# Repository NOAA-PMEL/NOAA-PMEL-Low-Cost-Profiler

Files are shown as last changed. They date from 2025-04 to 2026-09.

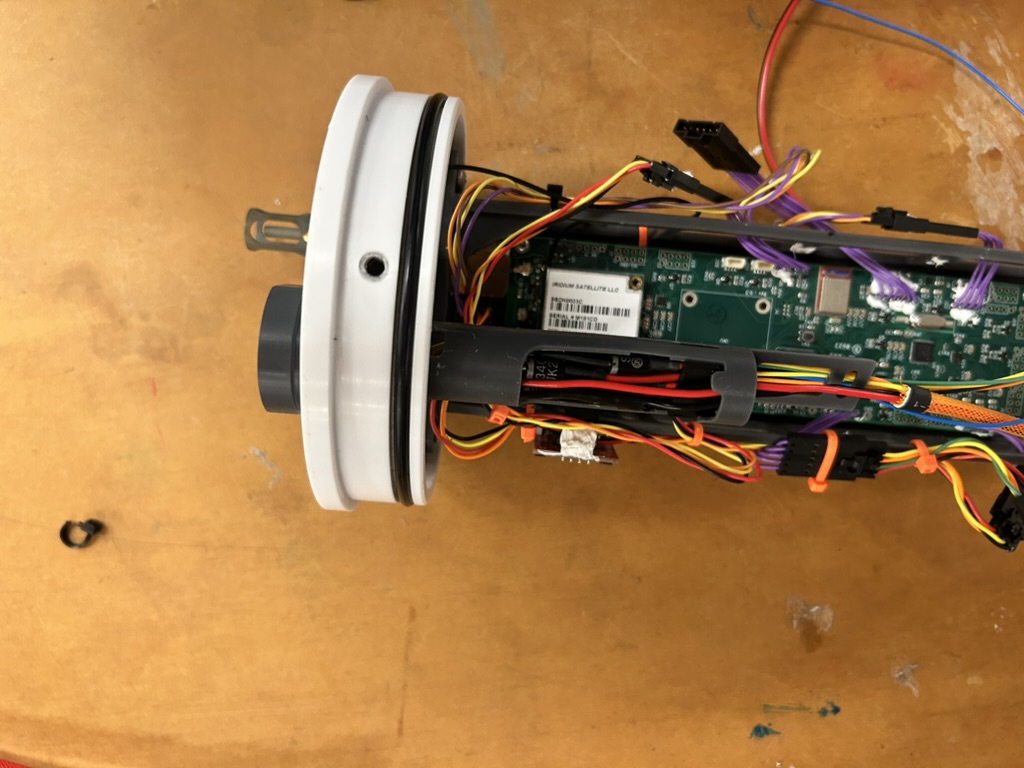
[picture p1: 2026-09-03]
Manual/UW Documents/Parts Photos/A83961EA-1B3E-4D60-9679-3123DDBCD0BC_1_105_c.jpeg

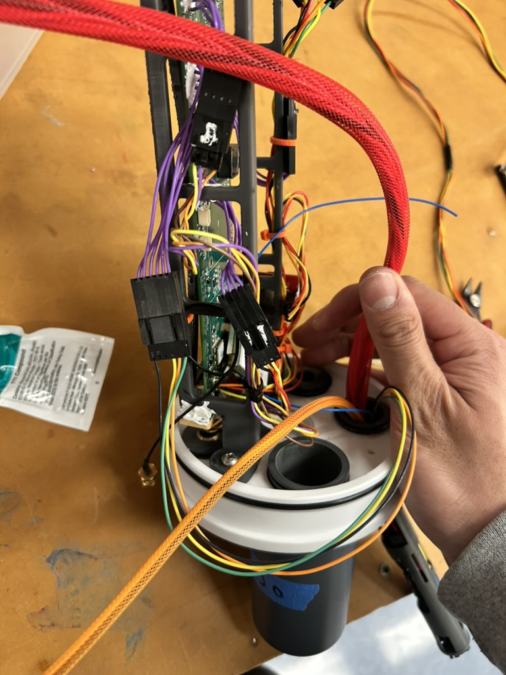
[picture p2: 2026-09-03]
Manual/UW Documents/Parts Photos/846BCBF3-054E-4CC3-9D93-AE1F20746E3C_1_105_c.jpeg

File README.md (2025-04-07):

# NOAA-PMEL Low Cost Profiler (LCP)
Open Source Repository for NOAA PMEL's Low Cost Profiler's mechanical design, firmware and electronics hardware.

# Attribution
You agree to acknowledge NOAA-PMEL on splash pages, and in publications, for products developed with this software.

# NOAA Legal Disclaimers
NOAA does not intend to patent this work, Low Cost Profiler (LCP) technology, worldwide. It may be used freely, but NOAA does not warrant its fitness for any use.

As a work of the United States Government, the associated schematics and software are in the public domain within the United States. Additionally, NOAA waives any potential copyright and related rights in the associated schematics and software worldwide through the Creative Commons Zero (CC0) 1.0 Universal Public Domain Declaration.

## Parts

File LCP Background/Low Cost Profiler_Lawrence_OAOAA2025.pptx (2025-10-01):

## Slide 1

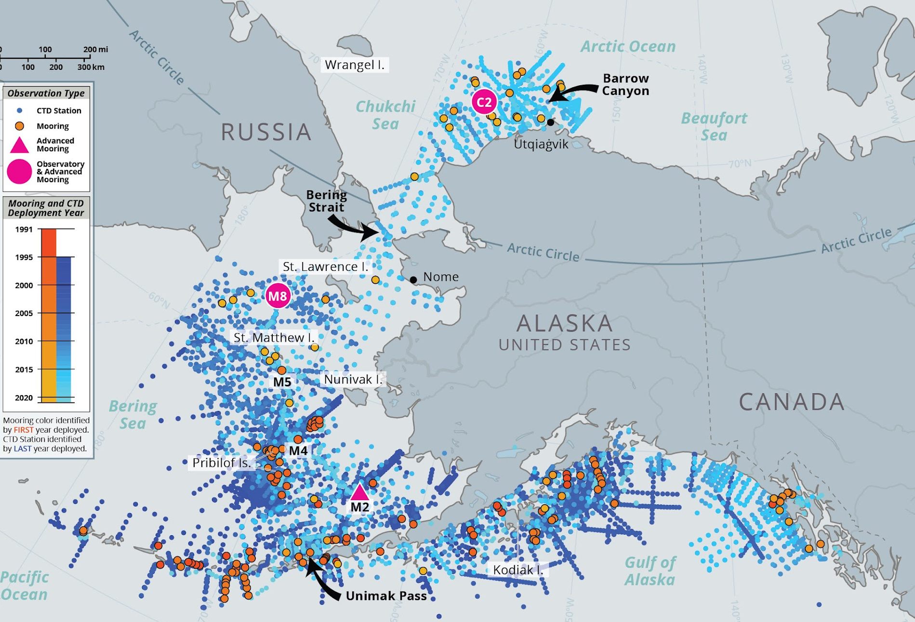
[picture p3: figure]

The Low Cost Profiler (LCP)
An affordable profiler to enable ocean science at scale

N.Lawrence¹, M. Casari², B.Martin¹, J.Kurina³
¹National Oceanic and Atmospheric Administration
²SeaMount Sensors & Automation, Waterbury, Vermont
³Cooperative Institute for Climate, Ocean, and Ecosystem Studies
PACIFIC MARINE ENVIRONMENTAL LAB | SEATTLE, WA

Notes: Mechanical Engineer at PMEL, what we do = design build and operate large global observational arrays = moorings
LCP was kickstarted by PMEL’s ITAE program = Innovative Technology for Arctic Exploration = Lab level, high risk High reward technology development funding to meet NOAA’s future ocean observation needs (other projects included Oculus and Saildrone)

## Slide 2

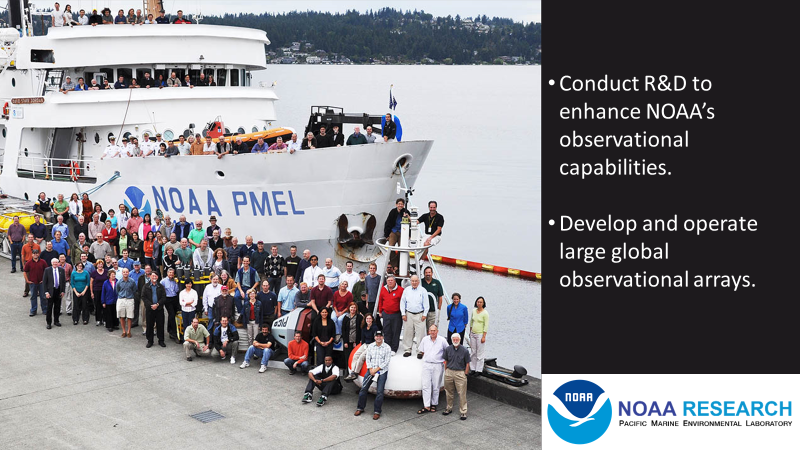
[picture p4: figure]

## Ocean Observation Tech Development: LCP

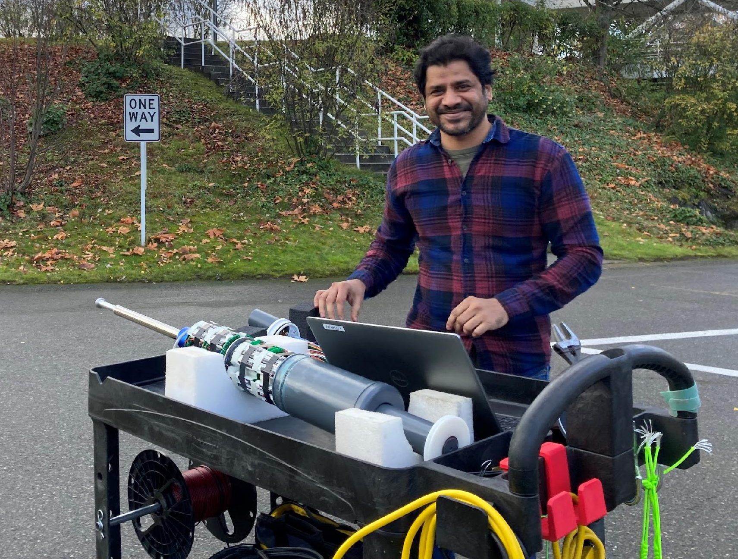
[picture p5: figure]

- LCP Product
- Science Applications
- Progress
- Future Plans/Needs

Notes: Quick rundown of this presentation

## Low Cost Profiler (LCP):

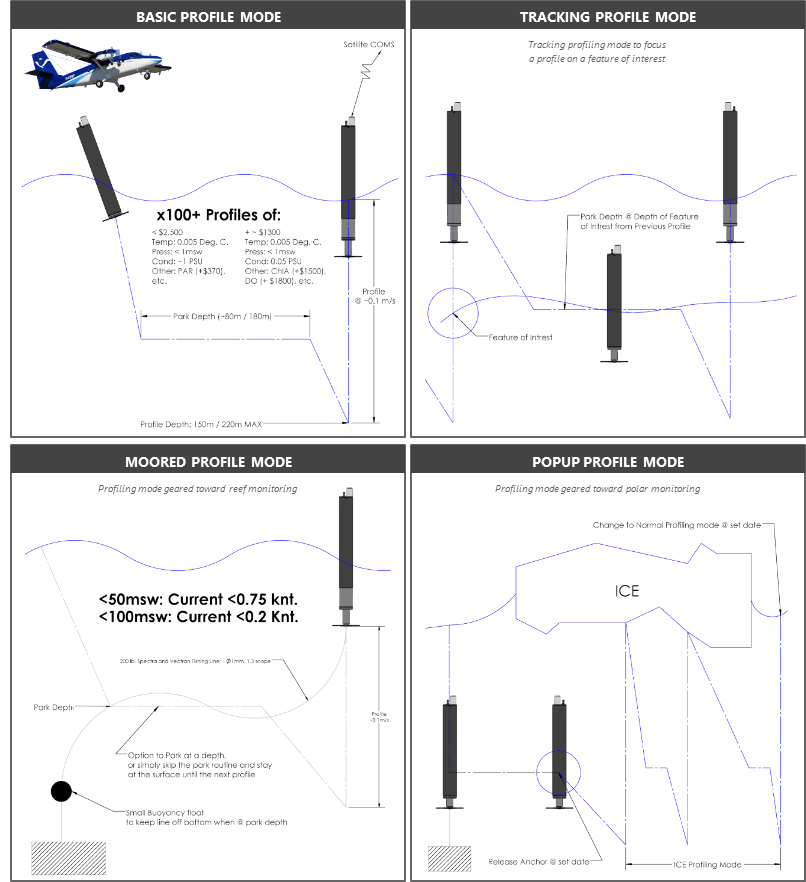
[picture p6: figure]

Cost | ~$5,000 (in QTYs of 10)
Maximum Depth | 220m
Endurance | 100 profiles (nominal)
Dimensions | 91.4 cm length x 12. 4 cm diameter
Weight | 13.6 kg
Telemetry | Iridium Short Burst Data (SBD) w/ more options available in future
Energy | Alkaline Battery Pack or Lithium
Features | Air deployable, Moorable
Sensors | Pressure: Keller 9LX-30Bar Temperature: S9 OEM Temp, RBRcoda* Conductivity:* S9 OEM CT, PMEL OEM, Aanderaa 5819 CHLA:* Turner Cyclops 7F PAR:* TAG-PARQ DO*: Aanderaa Optode 5730, PME microDOT

BASIC PROFILE MODE

BASIC PROFILE MODE

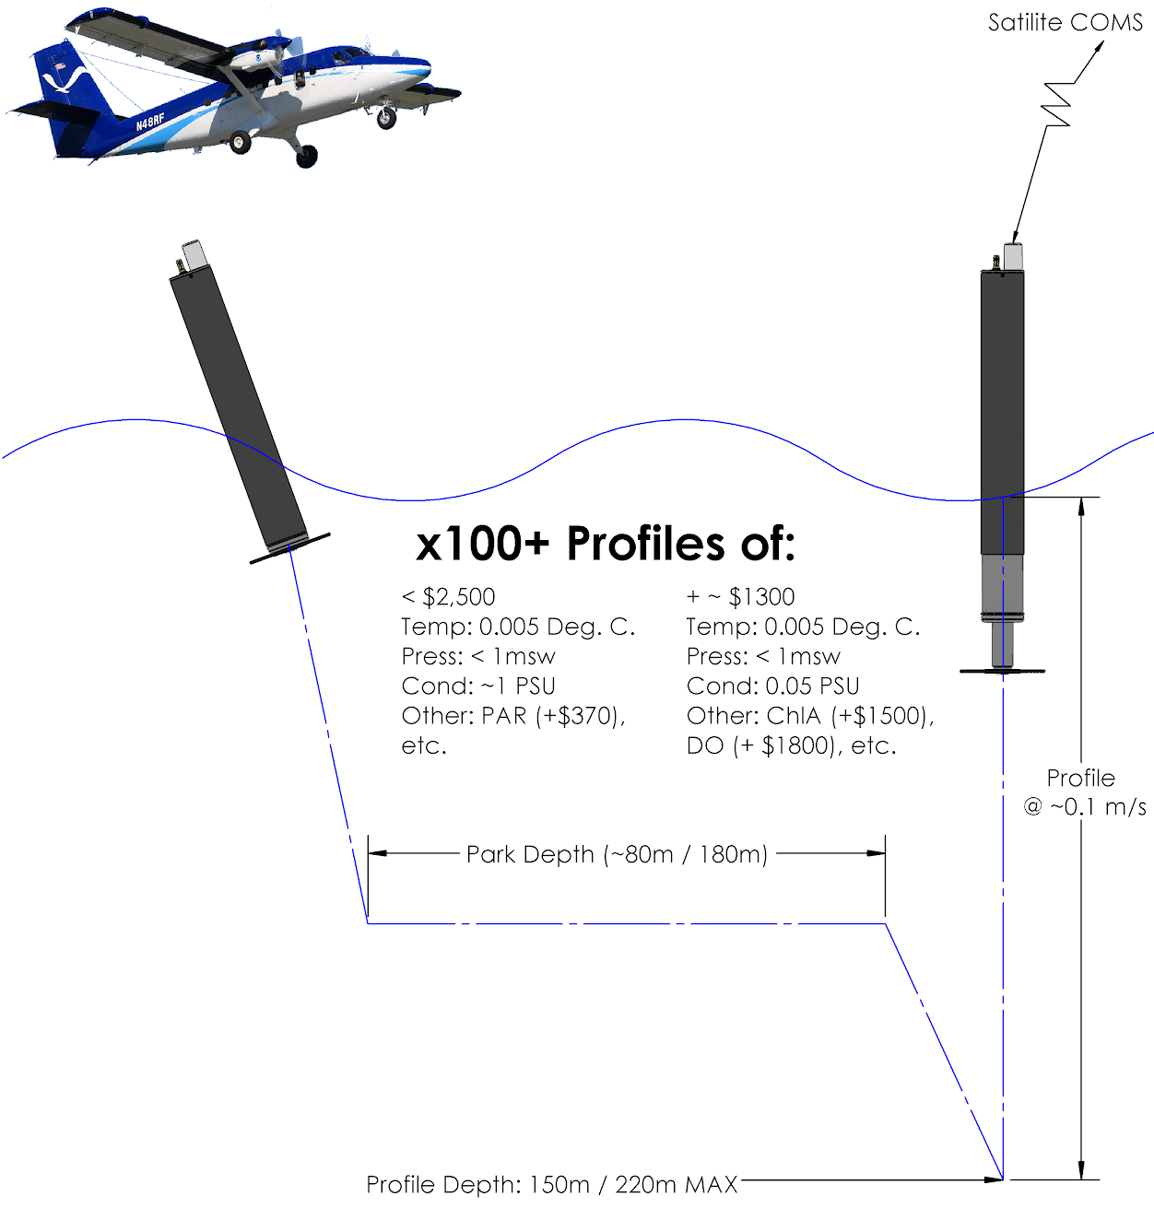
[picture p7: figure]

TRACKING PROFILE MODE

TRACKING PROFILE MODE

Tracking profiling mode to focus
a profile on a feature of interest

MOORED PROFILE MODE

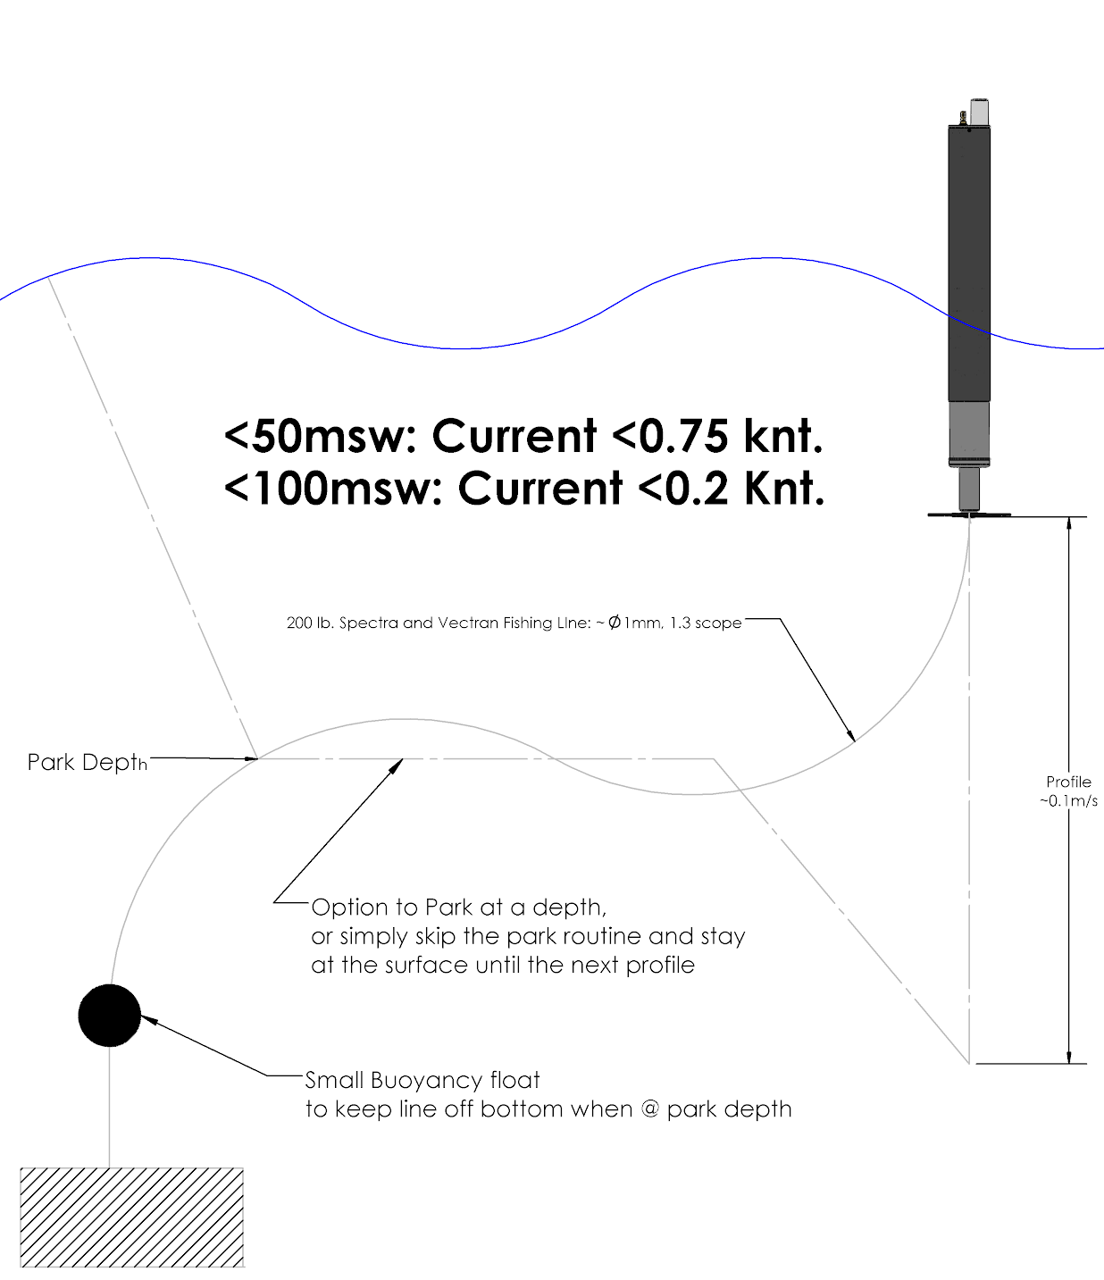
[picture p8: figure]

Profiling mode geared toward reef monitoring

POPUP PROFILE MODE

Profiling mode geared toward polar monitoring

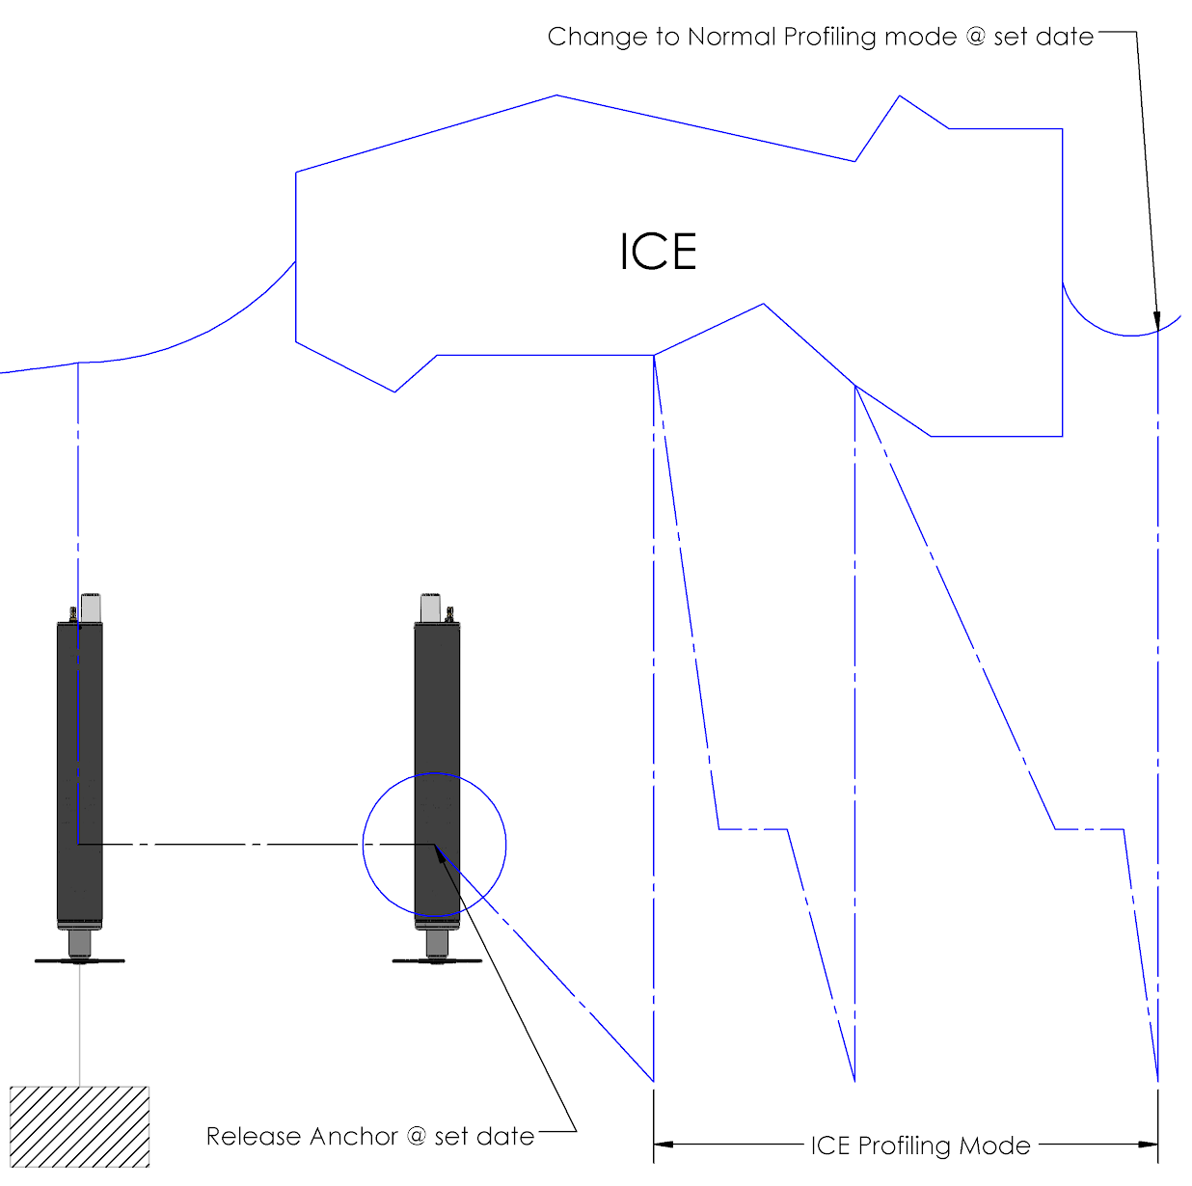
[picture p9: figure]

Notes: PMEL has developed the LCP, goal is to make a profile for <30$, an order of magnitude less than current profiling floats.
Developed to be easily built, configured, and deployed by air, ship or hand.
Simple Design = the LCP uses a direct-drive buoyancy engine to reduce mechanical complexity
Geared towards community involvement in sensor integration, goal is to bring your own sensor to an open source design that can be purchased from a contract manufacturer


The LCP can be configured pre-mission to perform in different observational roles, including drifting, timed release and moored, making it a unique tool for autonomously profiling the upper 200m of a water body.

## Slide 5

Low Cost Profiler (LCP): Sensors & Peripherals

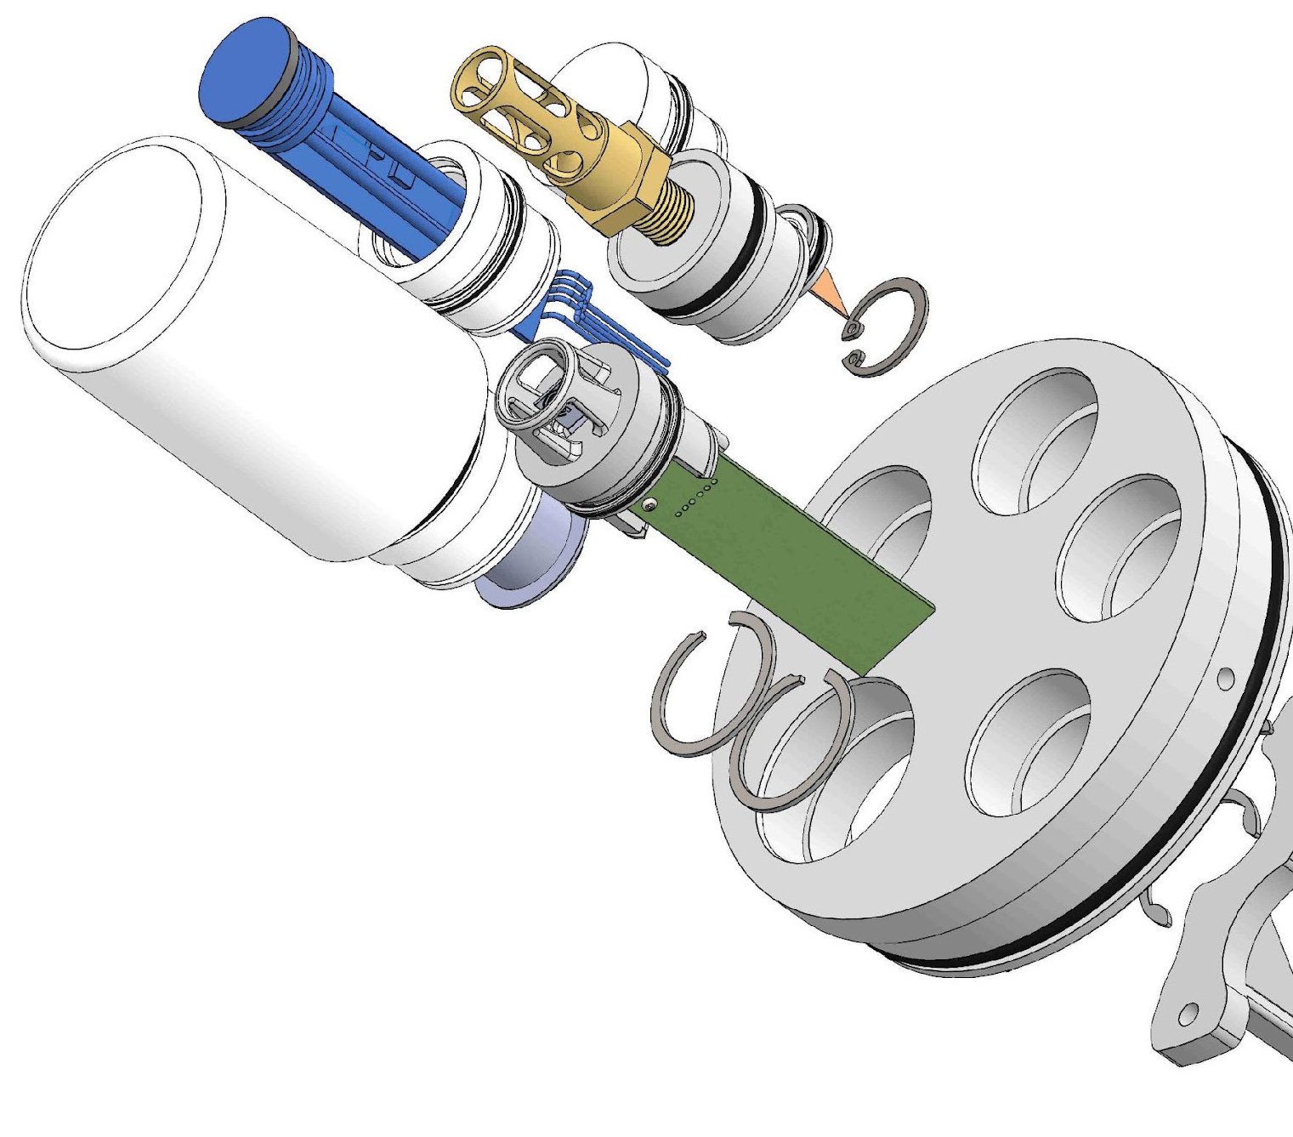
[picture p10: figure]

- OEM calibrated sensors
- 5 universal sensor ports
- Climate Quality
  - Temperature
  - Pressure
- ‘Weather’ Quality
  - Conductivity
  - CHL-A
  - PAR
  - DO
- Iridium SBD Communications

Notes: Key to reducing costs is using OEM manufacturer calibrated sensors

## LCP: Science Driven Applications

LCP Fills Gaps in Observational Arrays

Graphic Courtesy of Adrienne Sutton

- Hurricane Intensity
- Bering Sea Fisheries
- Arctic HABs and Ice
- Coastal & Coral Reef Monitoring
- ONR Profiling CTD BAA

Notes: Observation challenge = work to do to reduce the uncertainty in our predictive capability = opportunity for technology innovation in our flat funded world!
In response to this challenge, NOAA-PMEL is exploring innovative methods to quickly propagate and support high quality, low cost, tools throughout our community.
Requires the development of fit-for-purpose tools to fill gaps in our traditional observational array
LCP Solution =
Multi-mission capable = capitalize on economies of scale.
Keep costs low to allow for risk taking and rapidly scale in situ observations
Sensors are very expensive = make profiles
Profiling floats have proven successful at covering large volumes, ARGO like…. but much cheaper
Relevance & Application Examples: LCP has wide applicability to many NOAA R&D vision areas and the 2026 strategic research guidance memorandum
Vision Area 1: Hazardous and Extreme Weather = Hurricane Intensity
Vision Area 2: Sustainable fisheries
SRGM: improve coverage of observations = gap filling & Arctic & HAB

Here are a few we are actively pursuing that address , others? Let’s talk = rely on word of mouth for tech dissemination.

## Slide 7

LCP: Hurricane Application

GOAL: Subsurface ocean temperature and salinity measurements are needed ahead of and underneath hurricanes to:
- Initialize coupled forecast models
- Improve mixing parameterizations in models
- Aid forecaster situational awareness
- Improve understanding of hurricane air-sea interaction processes

Existing Technology:
- ALAMO Float = Expensive: ~$400K for 16 floats deployed ahead of Hurricanes Irma and Florence
- AxBT & AxCTD = Less expensive (~$1000) but only gives one temperature or CTD profile
Partner: AOML (Jun Zhang, Greg Foltz)

Three-dimensional cartoon of the temperature distribution in the upper ocean and the impact of a hurricane passing over the ocean when the oceanic mixed layer is thin like in the Gulf of Mexico and thick like the Caribbean Sea.

Credit: National Geographic

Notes: Hurricanes intensify by drawing heat energy from the ocean, Strong ocean mixing by a hurricane’s winds brings cooler water to the surface, decreasing the heat energy available to the hurricane
Air deployable LCP application

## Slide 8

LCP: Fisheries Application

GOAL: Improve understanding of regional oceanography and support fishing industry with tools that may reduce halibut bycatch

Need understand the connection between surface temperature and bottom temperature in the Kuskokwim Bay area, so that we may be able to use remotely-sensed surface temperature to predict real-time bottom temperature.
Partner: PMEL-ECOFOCI (Phyllis Stabeno, Calvin Mordy)


Predicting these bottom temperatures is difficult!
Measuring bottom temperature with LCP will support fishing industry


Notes:
Improve understanding of regional oceanography and (2) support fishing industry with predictive tools that may help reduce halibut bycatch
Yellowfin sole arrive earlier in colder water than halibut. To avoid halibut bi-catch it is necessary to predict (or measure) bottom temperatures. Allowing fishing vessels to arrive at fishing grounds when bottom temperatures are more optimal for yellowfin sole and less optimal halibut
Application for moored LCP, will trial this technology in Fall 2025

S = Spring when Yellowfin arrive on the inner shelf while temps are too cold for halibut. As things warm the fleet needs to move to colder water to avoid catching the halibut. Yellowfin move to deeper water if fall (F) and winter (W)

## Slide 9

Low Cost Profiler: Current Status


- Complete:
  - mechanical stress testing.
  - functional testing in tank.
  - Hand-deployed at RL5
- Now:
  - 5x field deployments moored in Puget Sound, WA.
  - Completed 100 profiles to 170m.
- Next Steps:
  - Secure stage 2 funding
  - CTD Sensor Integration
  - Air Deployment- ONR BAA
  - Open Source approach


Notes: Design is proven in PMEL pressure vessel and NOAA Dive Tower
Moored in Puget Sound
Next Steps = Secure funding for 2 focus areas for continued LCP tech development

## LCP expands work in the Beaufort Sea

LCP: Arctic Sea Ice Application

- Arctic AIR (Jiaxu Zhang, UW-CICOES) focuses on stratification mechanisms in the southern Beaufort Sea and their impact on sea ice formation/melt and phytoplankton growth.
- Previously, we relied on AxCTDs and ALAMO floats for this data, but LCP offers a more cost-effective alternative for measuring salinity-driven stratification.


2024 AxBT deployment along 150W


An ALAMO drifting down from Twin Otter

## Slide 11

Open Source Solution:

Societal implications of ocean change ≠ capacity of ocean technology development community


      - Use: Provide truly low-cost tool
- Scale: Contract manufacturer approach to building in quantities
- Sustain: Industry and users can assist in system upgrades, sensor integration…..


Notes:
Use LCP as a pilot for Open Source approach
Tool is not very useful if it is not available, how do we rapidly get the LCP technology into the hands of the broader scientific community?
Problem= Ocean observing technology development life cycles are too long!
Problem= Traditional commercialization path can result in expensive products that receive inadequate sustained development support
Problem = Sole source single points of failure =products often dropped due to lack of adequate commercial sales


Have been working with NOAA’s Tech Partnership office to:
Generate open source hardware license
Develop an open source technology transfer pathway in NOAA
Obtain permission to open source
MBARI has had a lot of luck with contract manufacturers producing complicated ocean sensors (pH), could be a solution to providing community with a source, this is what they are good at. Community ecosystem could then provide buying power, functionality upgrades
Risk = Do not know if it will work.

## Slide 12


Thank You

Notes:
Thank you!

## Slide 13


Low Cost Profiler (LCP): Design


- Simple direct drive buoyancy engine
- Maximizes OEM components
- Minimizes custom components

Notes: The LCP uses a direct-drive buoyancy engine to reduce mechanical complexity
And a commodity pressure housing taken from the industrial pneumatics industry

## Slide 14

ALAMO floats
Deployed ahead of hurricanes by aircraft
Can profile every 2 hours to 300 m for several months
Expensive: ~$400K for 16 floats deployed ahead of Hurricanes Irma and Florence

Sanabia and Jayne (2020)

Details are in the caption following the image

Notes: First row of colored circles indicates float deployment locations. Subsequent circles show surfacing locations of the floats, with colors indicating measured SST as the hurricane passed.

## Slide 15

AXBTs
Deployed ahead of hurricanes by aircraft
Floats on surface, releases thermistor probe that measures temperature as it drops
Less expensive (~$1000) but only gives one temperature profile
AXCTDs also measure salinity but are more expensive

Images showing an AXBT instrument and how the instrument is launched.

Credit: U.S. Coast Guard

NOAA Measures Hurricane Tammy from Satellites through the Sea

## LCP adds an additional platform for HAB monitoring

LCP: HAB Application

- Arctic AIR (Jiaxu Zhang, UW-CICOES) and collaborators are developing a multi-platform phytoplankton monitoring system to enable early warning of harmful algal blooms (HABs) in the Pacific Arctic.
- LCP with additional light and biological sensors (e.g, PAR, Chl-a) will greatly enhance data collection and help us better understand biophysical interactions and primary production.


LCP

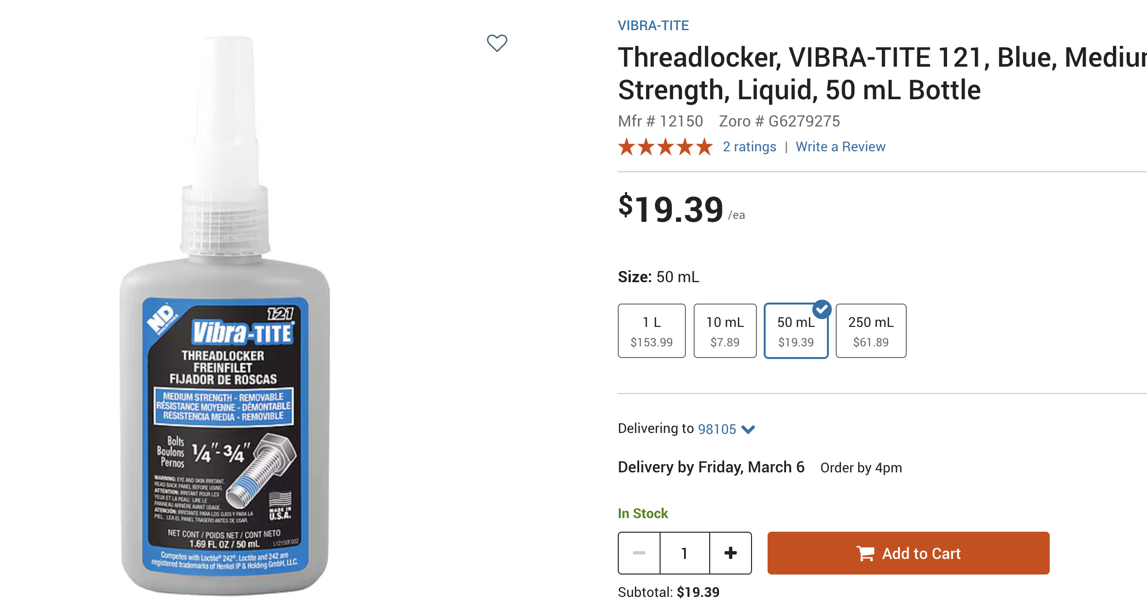
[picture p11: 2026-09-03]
Manual/UW Documents/Parts Photos/Screenshot 2026-03-04 at 11.32.21 AM.png

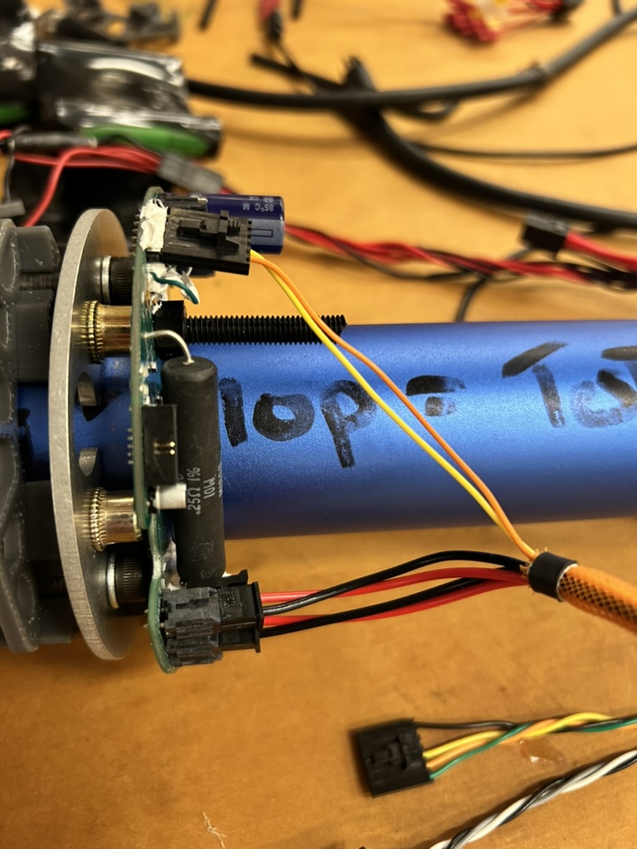
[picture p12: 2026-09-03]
Manual/UW Documents/Parts Photos/684DF367-D09E-419C-A230-30884F840D1B_1_105_c.jpeg

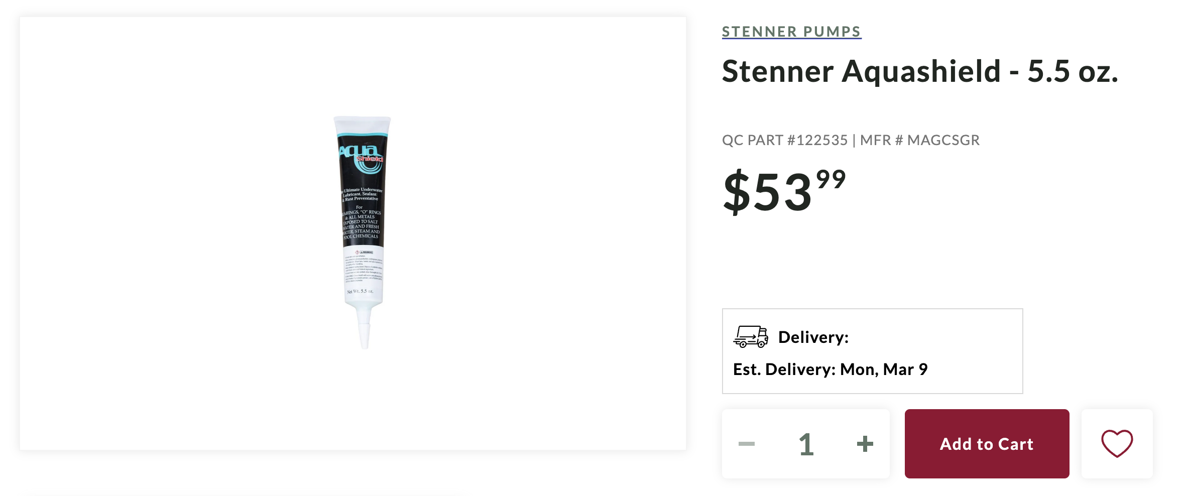
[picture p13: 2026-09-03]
Manual/UW Documents/Parts Photos/Screenshot 2026-03-04 at 11.31.39 AM.png

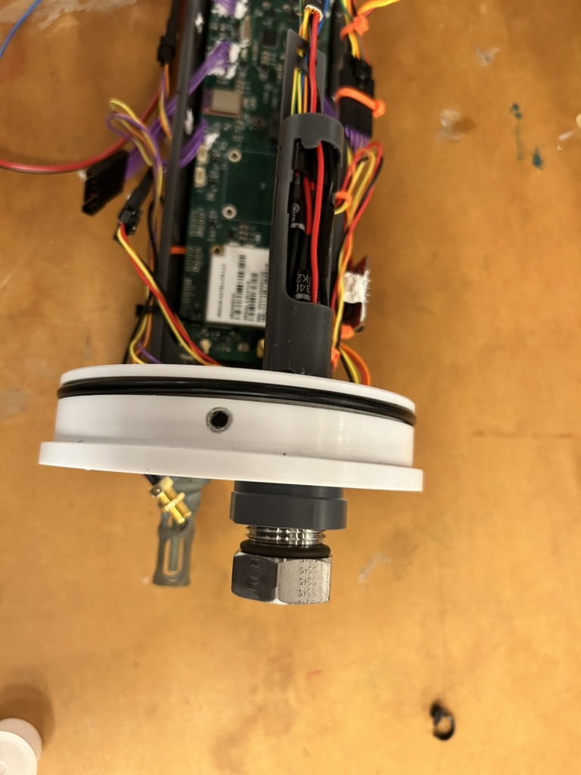
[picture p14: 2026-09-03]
Manual/UW Documents/Parts Photos/04B5F0DC-DED3-4595-93C2-F169555D24E7_1_105_c.jpeg

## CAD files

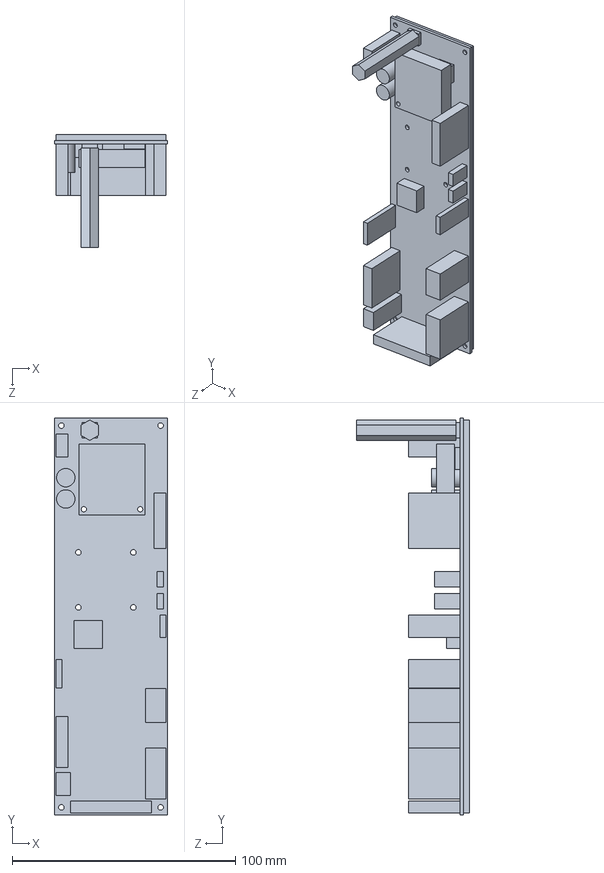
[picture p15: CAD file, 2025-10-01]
Mechanical/EDD Circuit Boards/R_Low Cost Profiler Main Control Board.sldprt
50.8 x 177.8 x 50.4 mm

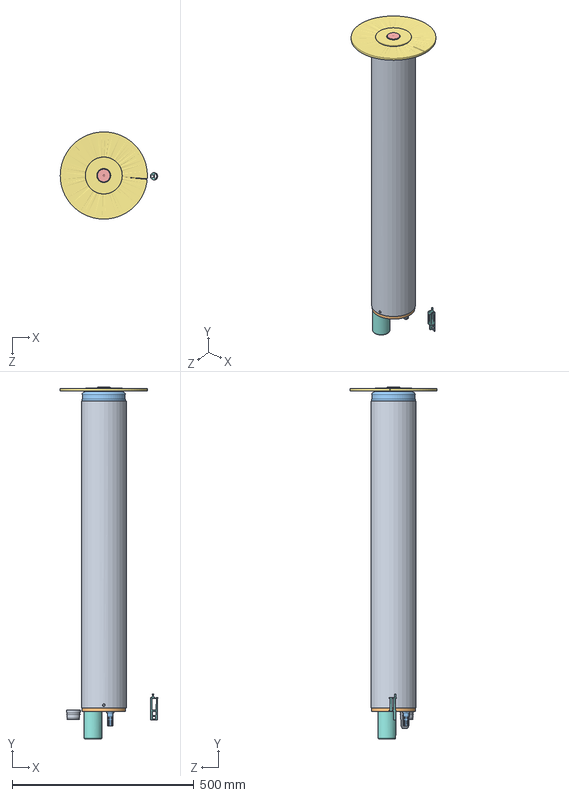
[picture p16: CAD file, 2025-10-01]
Mechanical/CAD Detail Parts/R_500140.sldasm
268.3 x 968.2 x 239.6 mm
FA-BH50-XXX-12-12
89U140341TT0667 x 2
98455A161_INTERNAL RETAINING RING
95105A183_ZINC-PLATED STEEL HEAVY-DUTY RIVET NUT x 8
Zeus_AA_ Alkaline_Battery x 72
Low Cost Profiler 9 Cell AA Battery Board x 16
92120A150_BRASS HEAT-SET INSERTS FOR PLASTIC x 66
92095A322_BUTTON HEAD HEX DRIVE SCREW x 66
91290A155_BLACK-OXIDE CLASS 12.9 SOCKET HEAD CAP SCREW x 4
91166A250_ZINC-PLATED STEEL FLAT WASHER x 4
90576A115_ZINC-PLATED CLASS 8 STL NYLON-INSERT LOCKNUT x 2
98455A224_INTERNAL RETAINING RING
97414A705_LOW CLEARANCE EXTERNAL RETAINING RING x 4
91650A490_18-8 SS SPIRAL EXTERNAL RETAINING RING
93369A141_NYLON HEX NUT x 4
Keller 9LX Pressure Sensor
92981A309_ALLOY STEEL SHOULDER SCREW
95610A370_NYLON PLASTIC WASHER_ x 4
2110-000-C-NH
92290A139_TYPE 316 SS SOCKET HEAD CAP SCREW x 2
HC600E
92131A630_SINGLETURN SPIRAL INTERNAL RETAINING RING x 2
98555A230_LOW-CLEARANCE EXTERNAL RETAINING RING
Low Cost Profiler Main Control Board
9452K840_OIL-RESISTANT BUNA-N MULTIPURPOSE O-RING x 4
9452K890_OIL-RESISTANT BUNA-N MULTIPURPOSE O-RING
9452K194_OIL-RESISTANT BUNA-N MULTIPURPOSE O-RING
94241A520_TYPE 316 STAINLESS STEEL SPLIT LOCK WASHER x 2
0307-PDT-H-093-0250 x 3
Parker_N4274_250_04000
Parker_N4274_250_02250
LFS1K011076WB010_6S
IST Conductivity Board
Low Cost Profiler Battery Power Management Board
SoundNine_Digital_OEM_Temperature_Sensor
SparkFun_Openlog_Qwiic
Maxtena_M1621HCT_P_SMA

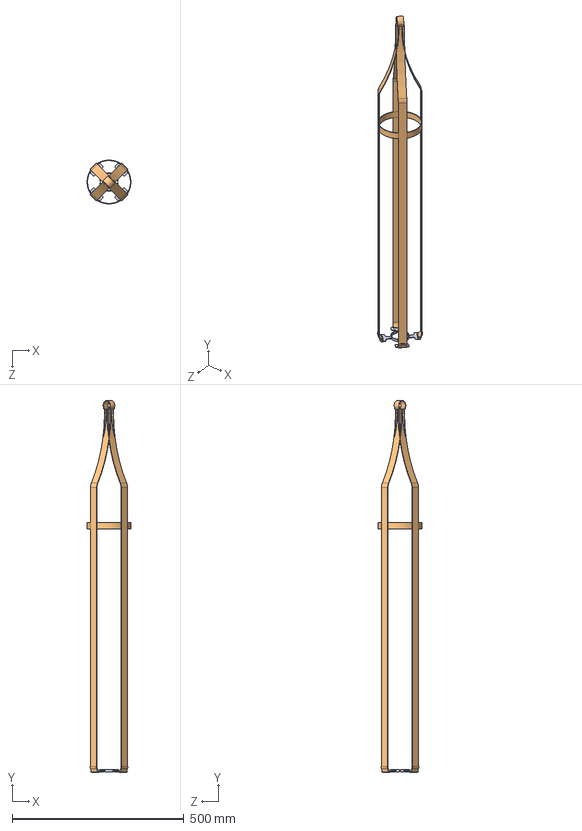
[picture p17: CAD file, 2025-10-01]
Mechanical/CAD Detail Parts/R_500151.sldasm
127.6 x 1082.7 x 127.6 mm

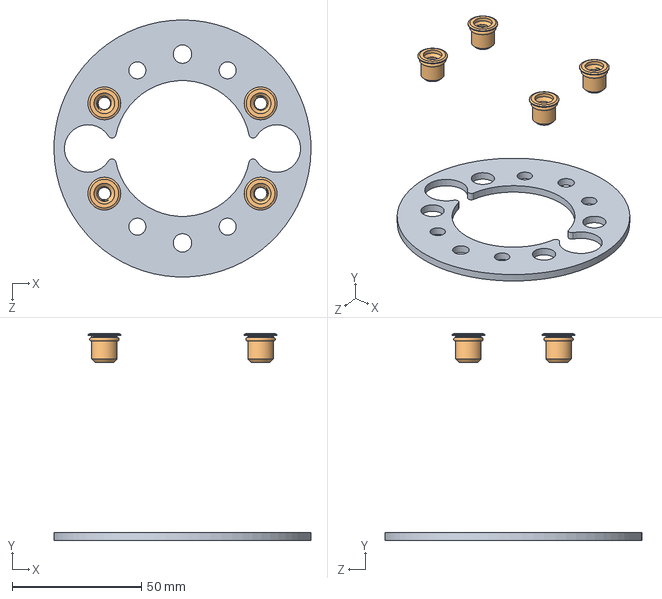
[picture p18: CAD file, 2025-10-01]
Mechanical/CAD Detail Parts/R_500142.sldasm
99.5 x 80.2 x 99.5 mm
95105A183_ZINC-PLATED STEEL HEAVY-DUTY RIVET NUT x 4

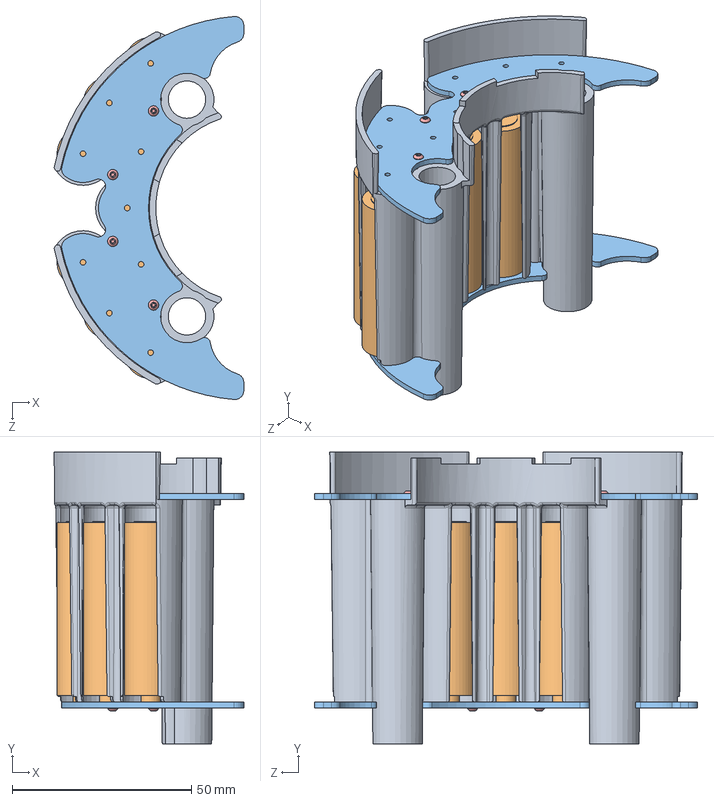
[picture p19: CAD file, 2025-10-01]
Mechanical/CAD Detail Parts/R_500147.sldasm
53.0 x 81.4 x 106.9 mm
Zeus_AA_ Alkaline_Battery x 9
Low Cost Profiler 9 Cell AA Battery Board x 2
92120A150_BRASS HEAT-SET INSERTS FOR PLASTIC x 8
92095A322_BUTTON HEAD HEX DRIVE SCREW x 8

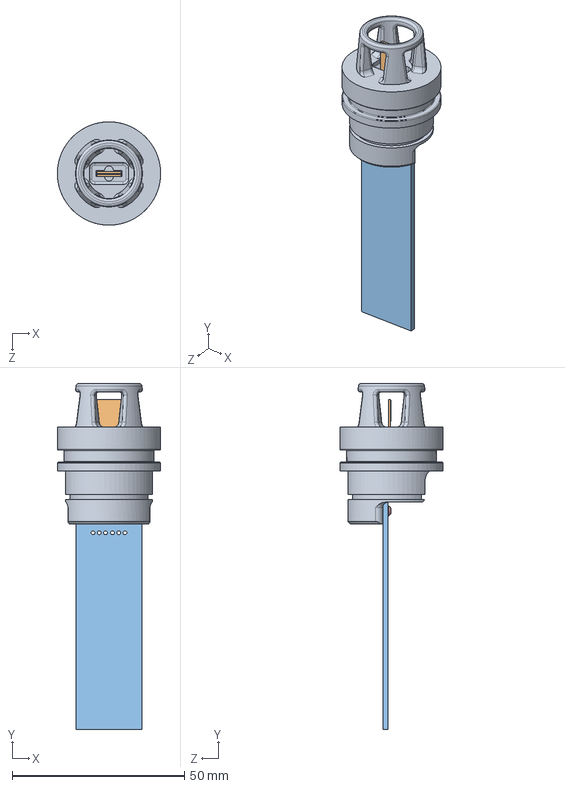
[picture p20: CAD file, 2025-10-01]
Mechanical/CAD Detail Parts/R_500126.sldasm
30.0 x 100.5 x 30.0 mm
LFS1K011076WB010_6S
IST Conductivity Board
92120A150_BRASS HEAT-SET INSERTS FOR PLASTIC x 2
92095A322_BUTTON HEAD HEX DRIVE SCREW x 2

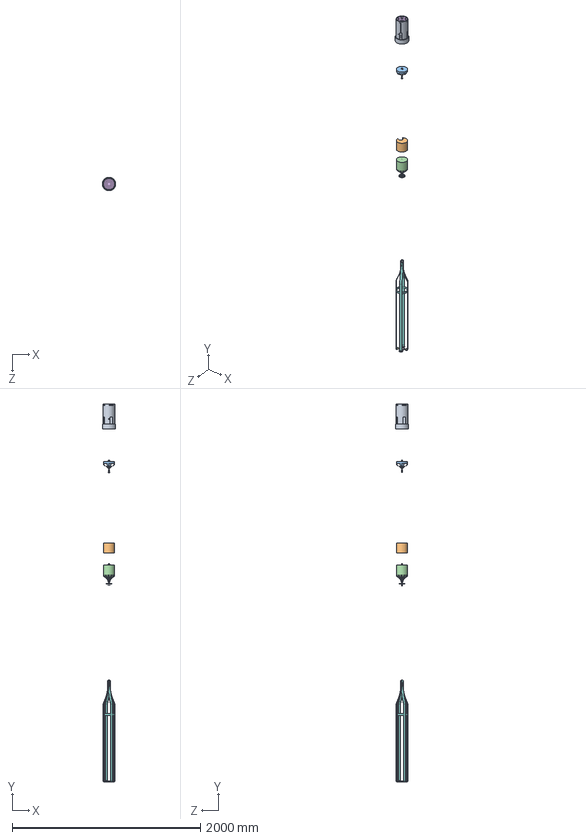
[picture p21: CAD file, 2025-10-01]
Mechanical/CAD Detail Parts/R_500150.sldasm
142.9 x 4012.2 x 143.0 mm
Rocketman_Pro-X_18in_Parachute
Rocketman_High Performance Chute_60in
3769T77_STAINLESS STEEL RING-NOT FOR LIFTING

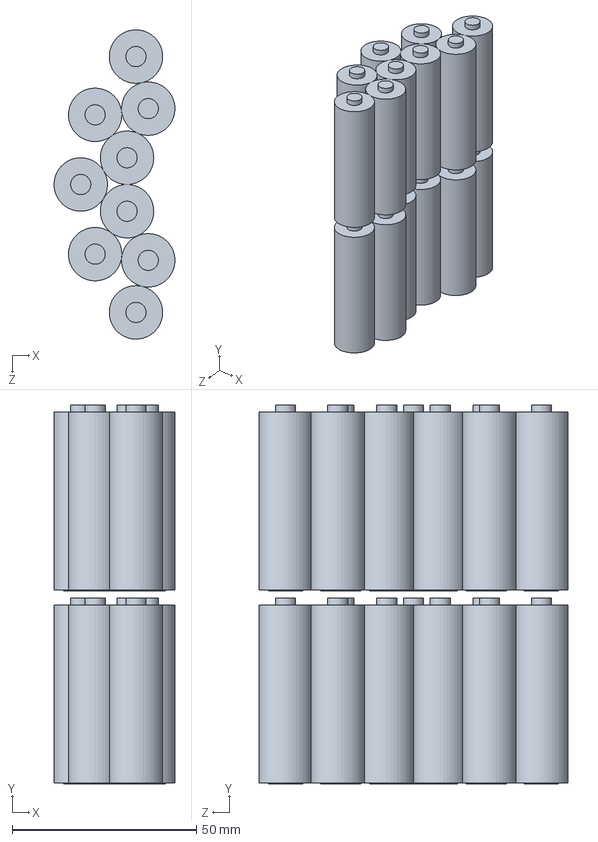
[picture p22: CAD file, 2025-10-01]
Mechanical/CAD Detail Parts/R_500146.sldasm
32.8 x 102.8 x 83.9 mm
Zeus_AA_ Alkaline_Battery x 18

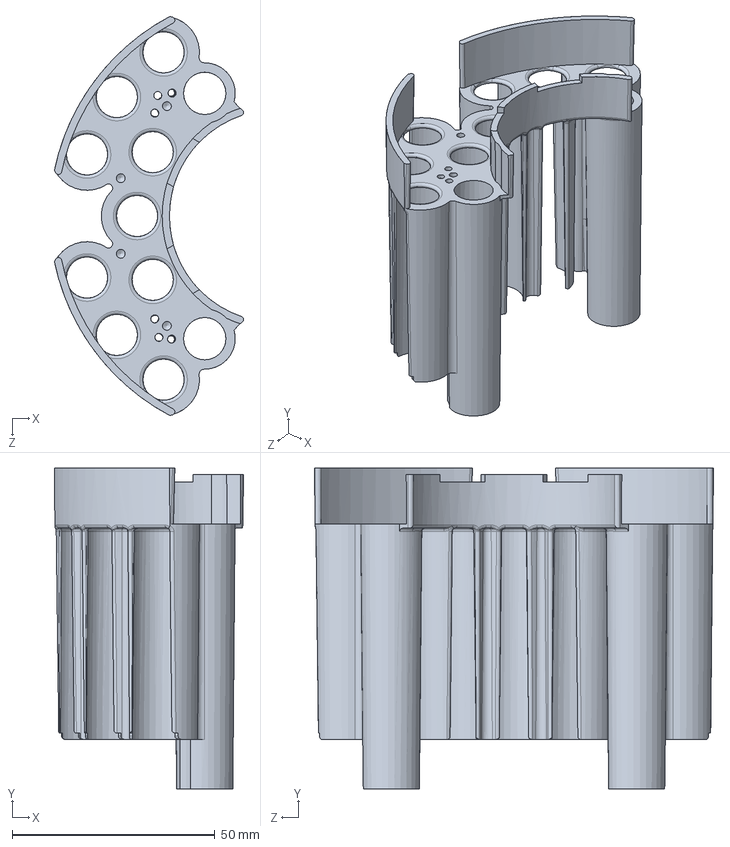
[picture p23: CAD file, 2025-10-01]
Mechanical/CAD Detail Parts/R_000550.SLDPRT
46.7 x 79.1 x 98.4 mm

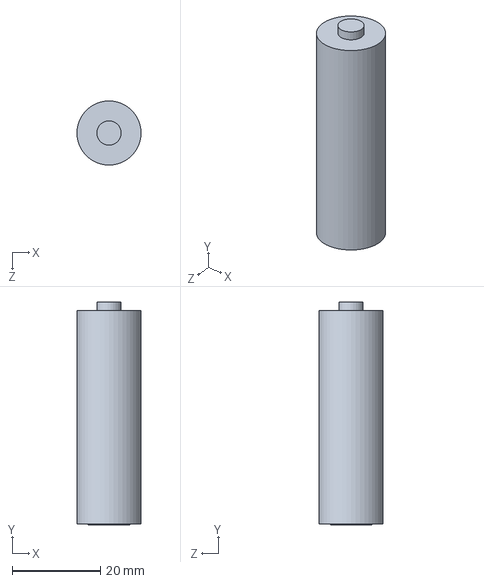
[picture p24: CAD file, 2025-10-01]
Mechanical/CAD OEM/R_Zeus_AA_ Alkaline_Battery.sldprt
14.5 x 50.4 x 14.5 mm

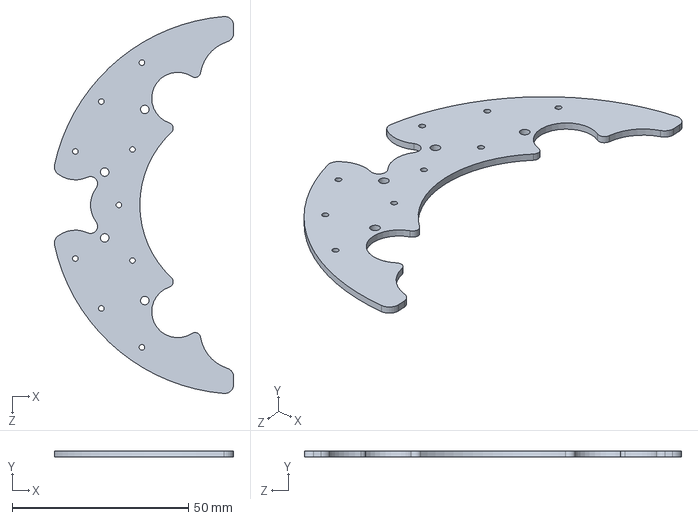
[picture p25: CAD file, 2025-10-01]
Mechanical/EDD Circuit Boards/R_Low Cost Profiler 9 Cell AA Battery Board.sldprt
50.9 x 1.60 x 106.9 mm

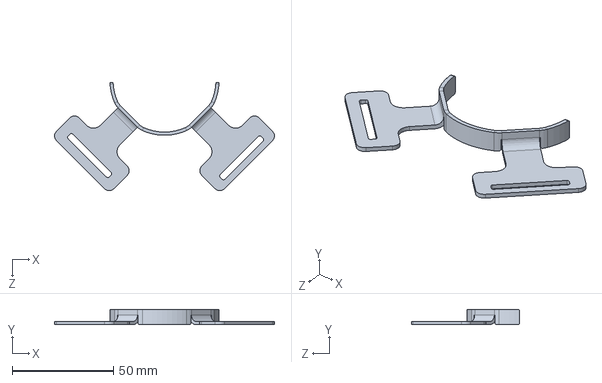
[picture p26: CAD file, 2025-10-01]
Mechanical/CAD Detail Parts/R_000561.SLDPRT
108.8 x 7.62 x 53.6 mm

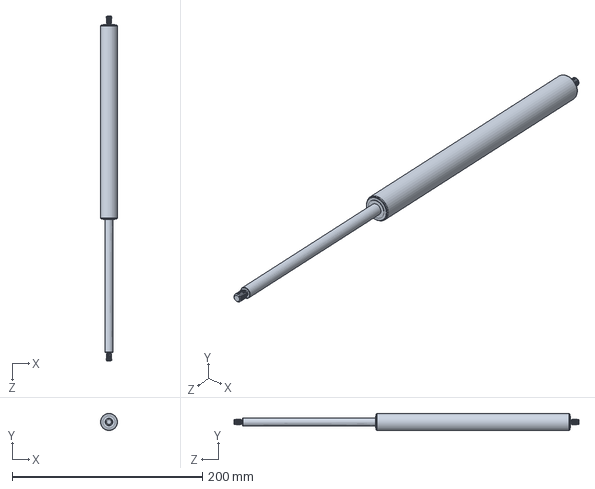
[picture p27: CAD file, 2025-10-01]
Mechanical/CAD OEM/R_89U140341TT0667.SLDPRT
18.0 x 18.0 x 362.9 mm

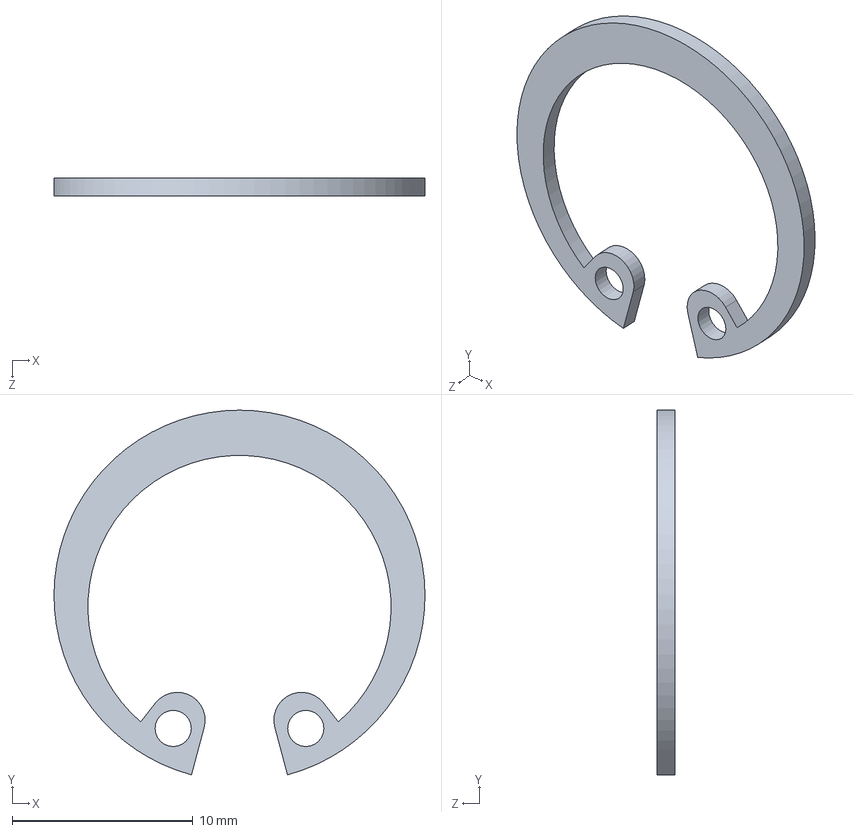
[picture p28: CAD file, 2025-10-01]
Mechanical/CAD OEM/R_98455A224_INTERNAL RETAINING RING.SLDPRT
20.5 x 20.2 x 1.00 mm

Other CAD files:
Mechanical/EDD Circuit Boards/R_002166.SLDPRT
Mechanical/CAD Detail Parts/R_000524.sldprt
Mechanical/EDD Circuit Boards/R_Low Cost Profiler Battery Power Management Board.SLDPRT
Mechanical/CAD Detail Parts/R_000549.sldprt
Mechanical/CAD Detail Parts/R_000450.SLDDRW
Mechanical/CAD Detail Parts/R_000450.sldprt
Mechanical/CAD Detail Parts/R_000521.SLDDRW
Mechanical/CAD Detail Parts/R_000521.sldprt
Mechanical/CAD Detail Parts/R_000522.SLDDRW
Mechanical/CAD Detail Parts/R_000522.sldprt
Mechanical/CAD Detail Parts/R_000524.SLDDRW
Mechanical/CAD Detail Parts/R_000525.SLDDRW
Mechanical/CAD Detail Parts/R_000525.sldprt
Mechanical/CAD Detail Parts/R_000529.SLDDRW
Mechanical/CAD Detail Parts/R_000529.sldprt
Mechanical/CAD Detail Parts/R_000531.SLDDRW
Mechanical/CAD Detail Parts/R_000531.sldprt
Mechanical/CAD Detail Parts/R_000532.SLDDRW
Mechanical/CAD Detail Parts/R_000532.sldprt
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

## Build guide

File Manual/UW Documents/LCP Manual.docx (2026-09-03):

# Table of Contents

Low-Cost Profiler Manual

Table of Contents -------------------------------------------------------- 1

Parts List ------------------------------------------------------------------ 2

Tool List ------------------------------------------------------------------- 3

Inner Assembly ---------------------------------------------------------- 4

Outer Assembly ---------------------------------------------------------- 5

Sensor Cap Assembly --------------------------------------------------- 6

Flashing the Control Board -------------------------------------------- 7

# Parts List

# Parts List

# Inner Assembly Parts:

Part Number | Part Name | Description | Stock size | Vendor+link | Quantity | image | Git number
1 | FA-BH50-XXX-12-12 | Firgelli Bullet Series 50 Cal. Linear Actuator, 12" stroke | FA-BH50-XXXX-12-12 | Firgelli Automation part site (https://www.robotshop.com/products/bullet-series-50-cal-linear-actuators-12v-500lb-12-inch?gad_source=1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) | 1 | | 4

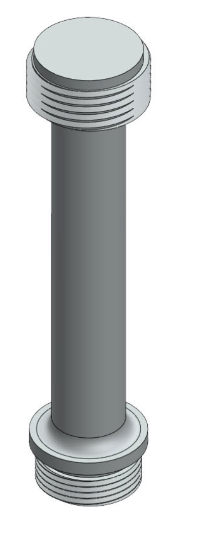
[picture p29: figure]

2 | Actuator Mount | Two sided threaded mount | | part file (https://github.com/NOAA-PMEL/NOAA-PMEL-Low-Cost-Profiler/blob/main/Mechanical/Mechanical%20Build%20Notebook/000532%20-%20Sheet1.pdf) | 1 | | 36

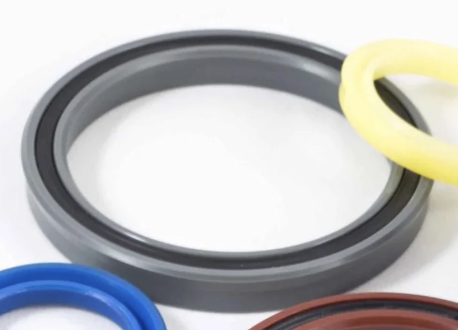
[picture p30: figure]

3 | N4274_250_02250 | 2.25" ID Parker PolyPak SPP Hydraulic Seal | N4274-250-02250 | Parker part link (https://www.parker.com/content/dam/Parker-com/Literature/Engineered-Polymer-Systems/EPS5370_PNLOOKUP.pdf) | 1 | | 46
4 | 000524 | Low Cost Profiler Piston #1 | PVC Type I Rod 1 | In house part file (https://github.com/NOAA-PMEL/NOAA-PMEL-Low-Cost-Profiler/blob/main/Mechanical/Mechanical%20Build%20Notebook/000524%20-%20Sheet1.pdf) | 1 | | 3
5 | N4274_250_04000 | 4" ID Parker PolyPak SPP Hydraulic Seal | N4274-250-04000 | Parker part link (https://www.parker.com/content/dam/Parker-com/Literature/Engineered-Polymer-Systems/EPS5370_PNLOOKUP.pdf) | 1 | | 45

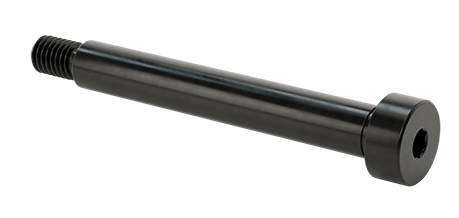
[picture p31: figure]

6 | 92981A309_ALLOY STEEL SHOULDER SCREW | M8 x 1.25mm, 10mm Dia x 70mm L, Shoulder Screw | 92981A309 | McMasterCarr part link (https://www.mcmaster.com/products/shoulder-screws/thread-size~m8-2/thread-pitch~1-25-mm/) | 1 | | 25

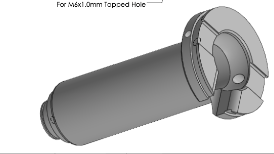
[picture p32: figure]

7 | 000525 | Low Cost Profiler Piston #2 | | part file (https://github.com/NOAA-PMEL/NOAA-PMEL-Low-Cost-Profiler/blob/main/Mechanical/Mechanical%20Build%20Notebook/000525%20-%20Sheet1.pdf) | 1 | | 5
8 | 0307-PDT-H-093-0250 | 7.31" Long 0307-PDT-H-093-0250 | 7.31" Long | Parker part link (https://ph.parker.com/us/en/product/cut-to-length-ptfe-wear-strip-for-pistons-pdt/0307-pdtb-02250-a-xxxx) | | | 42
9 | 0307-PDT-H-093-0250 | 11.44" Long 0307-PDT-H-093-0250 | 11.44" Long | Parker part link (https://ph.parker.com/us/en/product/cut-to-length-ptfe-wear-strip-for-pistons-pdt/0307-pdtb-02250-a-xxxx) | | | 44

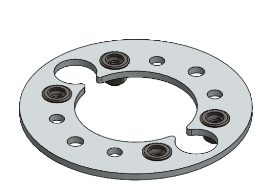
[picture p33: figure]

10 | 500142 | Low Cost Profiler Gas Spring Ring | | Part file (https://github.com/NOAA-PMEL/NOAA-PMEL-Low-Cost-Profiler/blob/main/Mechanical/Mechanical%20Build%20Notebook/500142.pdf) | 2 | | 13
11 | 98455A161 | 100mm Steel Internal Retaining Ring | MMC# 98455A161 | McMasterCarr part link (https://minibearings.com/products/100x103-5x3-internalcirclips-cci10000c) | 1 | | 7
12 | 89U140341TT0667 Gas Springs | IGS 8/18 x 140mm Gas Spring | | Industrial Gas Spring part link (https://www.raptorsupplies.com/pd/spd/89u140341tt0667) | 2 | | 6
13 | 90576A115 | M6 x 1mm, Medium-Strength Steel Nylon-Insert Locknut | 90576A115 | McMaster Carr part link (https://www.mcmaster.com/products/class-8-steel-hex-nuts/locknuts-2~/?s=class-8-steel-hex-nuts) | 2 | | 17
14 | 91290A155 | M6 x 1mm , 200mm L, Alloy Steel Socket Head Screw | MMC# 91290A155 | McMaster Carr part link (https://www.mcmaster.com/products/socket-head-screws/length~200-mm/) | 1 | | 15
15 | 91166A250 | M6 , 6.4 mm ID, 12 mm OD, Zinc-Plated Steel Washer | MMC# 91166A250 | McMaster Carr part link (https://www.mcmaster.com/products/washers/washers-2~washer-type~flat/) | 4 | | 16
16 | Note: add something about the battery holders and inserting the batteries.
17 | Low Cost Profiler Battery Power Management Board | Low Cost Profiler Battery Power Management Board | | | 1 | | 53
18 | Low Cost Profiler Battery Rod 000542 | M6 x 1.0mm Nylon 6/6 Threaded Rod 6.25" Long | MMC# 98882A249 | McMaster Carr part link (https://www.mcmaster.com/products/threaded-rods/thread-size~m6-2/material~nylon-6-6-1/) | 4 | | 48
19 | 93369A141 | M6 x 1mm, Nylon Hex Nut | MMC# 93800A600 | McMaster Carr part link (https://www.mcmaster.com/products/hex-nuts/thread-size~m6-2/?s=m6+x+1mm%2C+nylon+hex+nut) | 4 | | 23
20 | 95610A370_NYLON PLASTIC WASHER_ | M6, 6.4mm ID, x 12mm OD, Nylon Plastic Washer | MMC# 95610A570 | McMaster Carr part link (https://www.mcmaster.com/products/washers/screw-size~m6/washers-2~/) | 4 | | 27

Endcap Assembly:

Item Number | Part Number | Description | Description | Vendor Link | Image Link
21 | 98455A224 | 19mm ID Internal Retaining Ring, Black-Phosphate Spring Steel | MMC# 98455A224 | McMaster Carr part link (https://www.mcmaster.com/98455A224/)
22 | 97414A705 | 1" OD Low-Clearance External Retaining Ring, Spring Steel | MMC# 97414A705 | McMaster Carr part file (https://www.mcmaster.com/97414A705/)

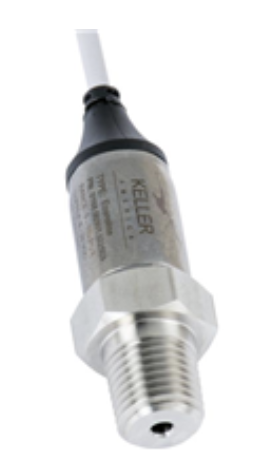
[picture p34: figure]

23 | Keller 9LX | Keller 9LX 30 Bar OEM Pressure Sensor | 9LX-30 Bar | Keller America part link (https://www.digikey.com/en/products/detail/keller-america-inc/0169-00703-022503/13530383?gclsrc=aw.ds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)
24 | 000547 | Low Cost Profiler Antenna Housing | Type 1 | In-house part file (https://github.com/NOAA-PMEL/NOAA-PMEL-Low-Cost-Profiler/blob/main/Mechanical/Mechanical%20Build%20Notebook/000547%20-%20Sheet1.pdf)
25 | 92290A139 | M4 x 0.7mm Thread, 6mm L, 316 SS Socket Head Screw | MMC# 92290A139 | McMaster Carr
26 | HC600E | Tallysman OEM Iridium Helix Antenna | HC600E | Tallysman Wireless

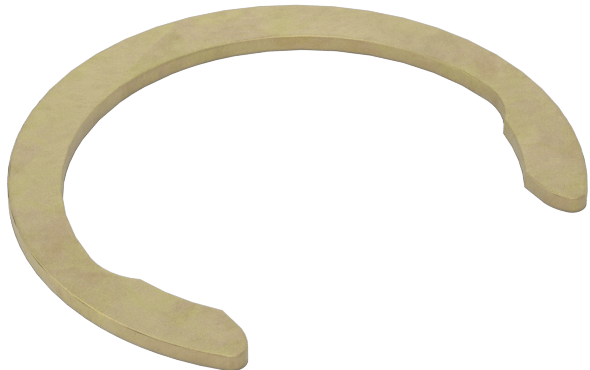
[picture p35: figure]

28 | 98555A230 | 1-3/8" OD Side-Mount External Retaining Ring, Steel | MMC# 98555A230 | McMaster Carr part link (https://www.mcmaster.com/98555A230/)
33 | 92131A630 | 28mm ID Single-Turn Spiral Internal Retaining Ring, 1090 Spring Steel | MMC# 92131A630 | McMaster Carr part link (https://www.mcmaster.com/92131A630/)
36 | Low Cost Profiler Main Control Board | Low Cost Profiler Main Control Board | | In-House
37 | 9452K84 | 2-120 Buna N O-Ring 4 | 2-120, MMC# 9452K84 | McMaster Carr part link (https://www.mcmaster.com/9452K84/)
38 | 9452K89 | 2-125 Buna N O-Ring 1 | 2-125, MMC# 9452K89 | McMaster Carr part link (https://www.mcmaster.com/9452K89/)
39 | 9452K194 | 2-244 Buna N O-Ring 1 | 2-244, MMC# 9452K194 | McMaster Carr part link (https://www.mcmaster.com/9452K194/)
40 | 000531 | RBR Coda Sensor Port | Type 1 | part file (https://github.com/NOAA-PMEL/NOAA-PMEL-Low-Cost-Profiler/blob/main/Mechanical/Mechanical%20Build%20Notebook/000531.pdf)
41 | 000531 | 9LX Pressure Port | Type 1 | part file (https://github.com/NOAA-PMEL/NOAA-PMEL-Low-Cost-Profiler/blob/main/Mechanical/Mechanical%20Build%20Notebook/000531.pdf)
42 | 000531 | 7/16-20 Threaded Port 1 | Type 1 | part file (https://github.com/NOAA-PMEL/NOAA-PMEL-Low-Cost-Profiler/blob/main/Mechanical/Mechanical%20Build%20Notebook/000531.pdf)
43 | 000531 | Turner Cyclops CHLA Sensor Port | Type 1 | part file (https://github.com/NOAA-PMEL/NOAA-PMEL-Low-Cost-Profiler/blob/main/Mechanical/Mechanical%20Build%20Notebook/000531.pdf)
44 | 2110-000-C-NH | Turner Cyclops 7F CHLA, No Housing OEM 1 | Cyclops 7F- No Housing Version | Turner Designs Inc. part link (https://www.turnerdesigns.com/cyclops-7f-submersible-fluorometer)
45 | 500126 | LFS1107 Conductivity Sensor 1

Outer Assembly Parts:

Item Number | Part Name | Step used | Description | Vendor Link | Image Link
46 | 000521 | 2, 5, 7, 10, 11, 12 | LCP Housing | Amalga Composites
47 | 000522 | 9, 11, 12, 13 20 | LCP Instrument endcap | 522 (https://github.com/NOAA-PMEL/NOAA-PMEL-Low-Cost-Profiler/blob/main/Mechanical/Mechanical%20Build%20Notebook/000522%20-%20Sheet1.pdf)
48 | 91650A490 | 16 21 | 1-3/8" OD, Heavy Duty Spiral External Retaining Ring, 18 8 Stainless Steel | McMaster Carr
49 | 000539 | 14, 15, 16 29 | LCP Brush Drag Plate Retainer | 0539 (https://github.com/NOAA-PMEL/NOAA-PMEL-Low-Cost-Profiler/blob/main/Mechanical/Mechanical%20Build%20Notebook/000539%20-%20Sheet1.pdf)
50 | 000546 | 15 31 | Low Cost Profiler Drag Brush | Memtech Inc.
51 | 92290A139 | 13 36 | M4 x 0.7mm Thread, 6mm L, Socket Head Screw | McMaster Carr https://www.mcmaster.com/91290A139/
52 | 000532 | 8, 9, 41 | Low Cost Profiler Actuator Mount | 532 (https://github.com/NOAA-PMEL/NOAA-PMEL-Low-Cost-Profiler/blob/main/Mechanical/Mechanical%20Build%20Notebook/000532%20-%20Sheet1.pdf)
53 | 94241A520 | 13 | M4 Split Lock Washer, 4.4mm ID x 7mm OD, 316 Stainless Steel | McMaster Carr

# Tool List and Installation Tools

# Tool List + Installation Tools

Inner Assembly and Installation Tools

Tool/Adhesive number | Step Used | Tool description | Vendor | Image

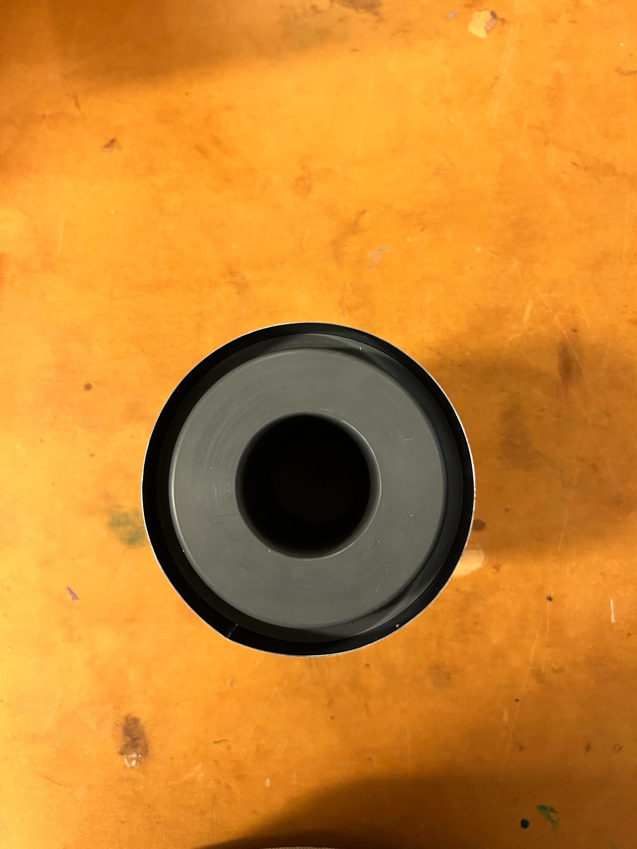
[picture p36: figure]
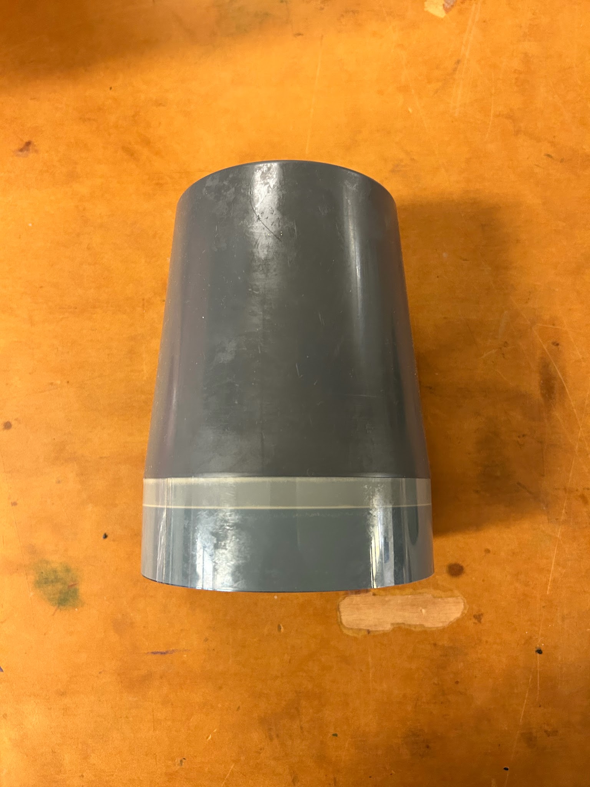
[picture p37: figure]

1 | Step 4: Install seal #45 onto piston #3 | Piston1 Seal Installation Tool A Assembly, 500195 | In-house build

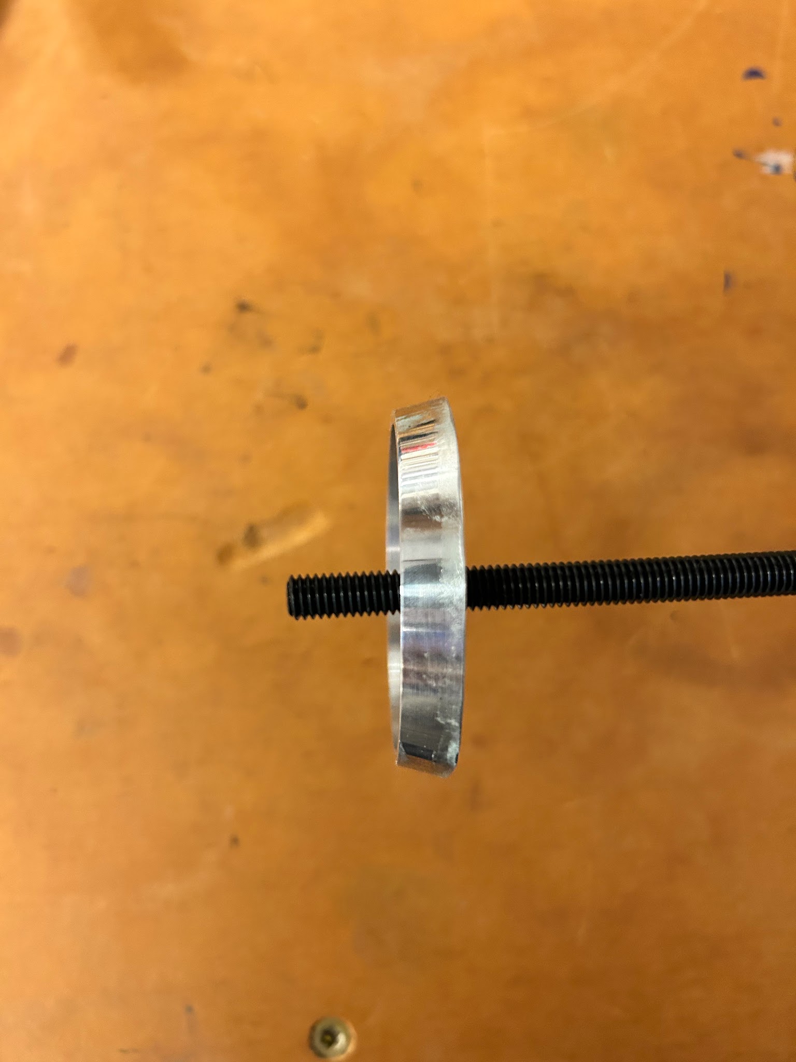
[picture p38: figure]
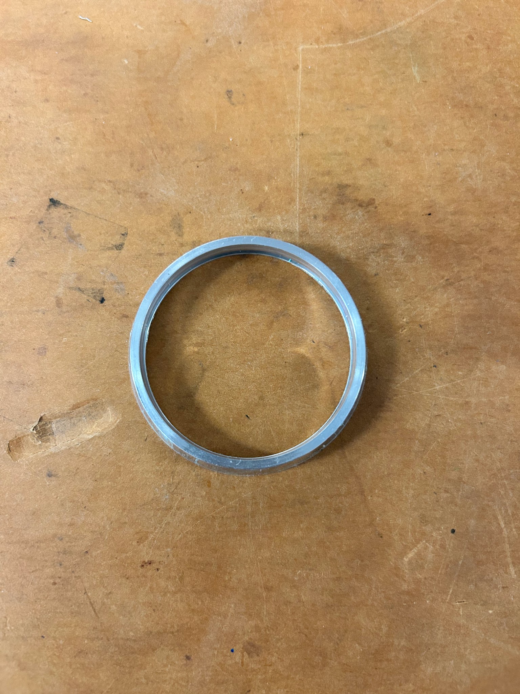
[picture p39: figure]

2 | Steps 8 & 11: Install onto #5 before inserting into #3, then remove after | Piston2 Seal Installation Tool, 000574
3 | Step 14: Installing #7 retaining ring to secure #13 to #3 | Large Internal Retaining Ring pliers | https://www.mcmaster.com/5391A37/

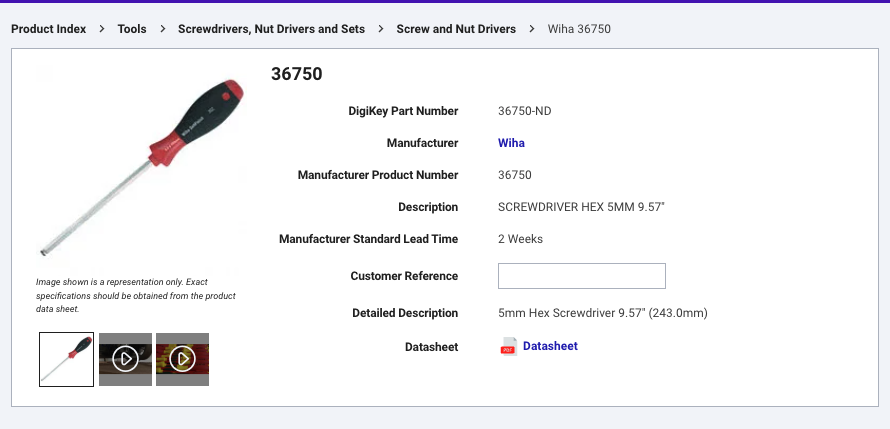
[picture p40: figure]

4 | Steps 17: Bolting upper #13 assemblies with #15 4x | 5mm hex drive screwdriver | 5mm screwdriver (https://www.digikey.com/en/products/detail/wiha/36750/511083?gclsrc=aw.ds&gad_source=1&gad_campaignid=20232005509&gbraid=0AAAAADrbLlgR33g_0IEcxBuh_0exNC-bO)

Adhesive and Consumables

Tool# | Step Used | Adhesive/Consumable | Vendor | Image

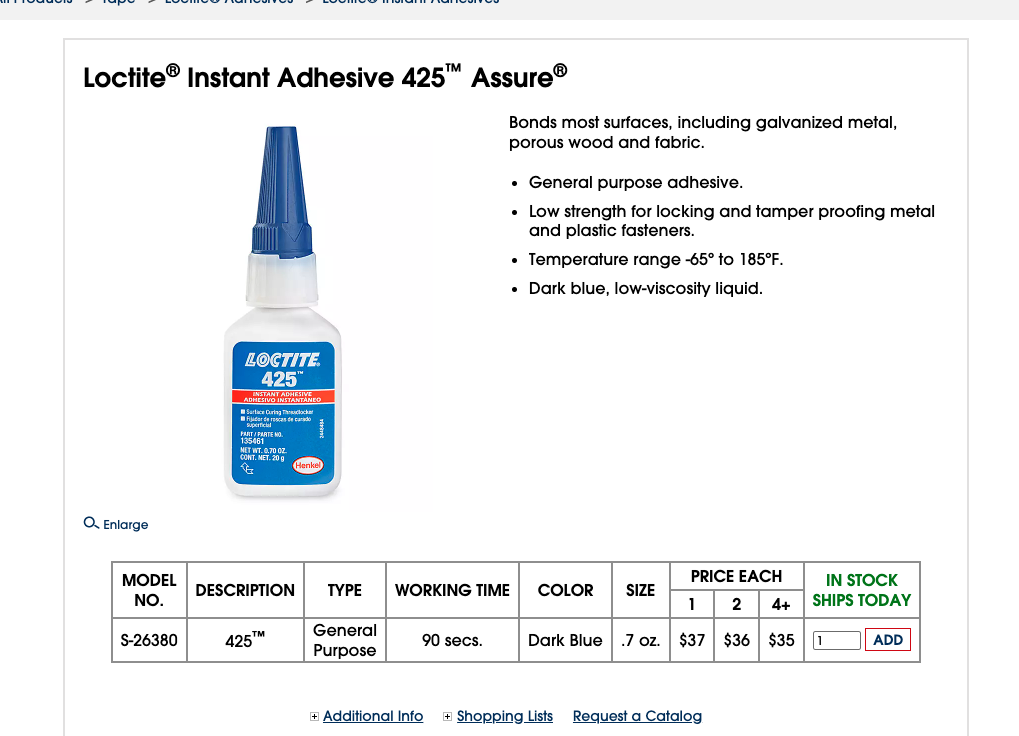
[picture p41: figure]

T5 | Steps 2, 5, 17, 20–21: Coating #36 before screwing into #4; cleaning and coating #25 threads; coating #15 threads before installing through upper #13 | Loctite 425 Threadlocker | Loctite threadlocker (https://www.uline.com/Product/Detail/S-26380/Loctite-Adhesives/Loctite-Instant-Adhesive-425-Assure?pricode=WB0948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)
T6 | Steps 3, 4, 7: Installing #46 into #3; installing #45 onto #3; greasing bore of #3 and OD of #5 before inserting piston | Aquashield Waterproof Grease | Aqua Shield (https://www.qcsupply.com/products/stenner-aquashield-5-5-oz?variant=51003288256819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)

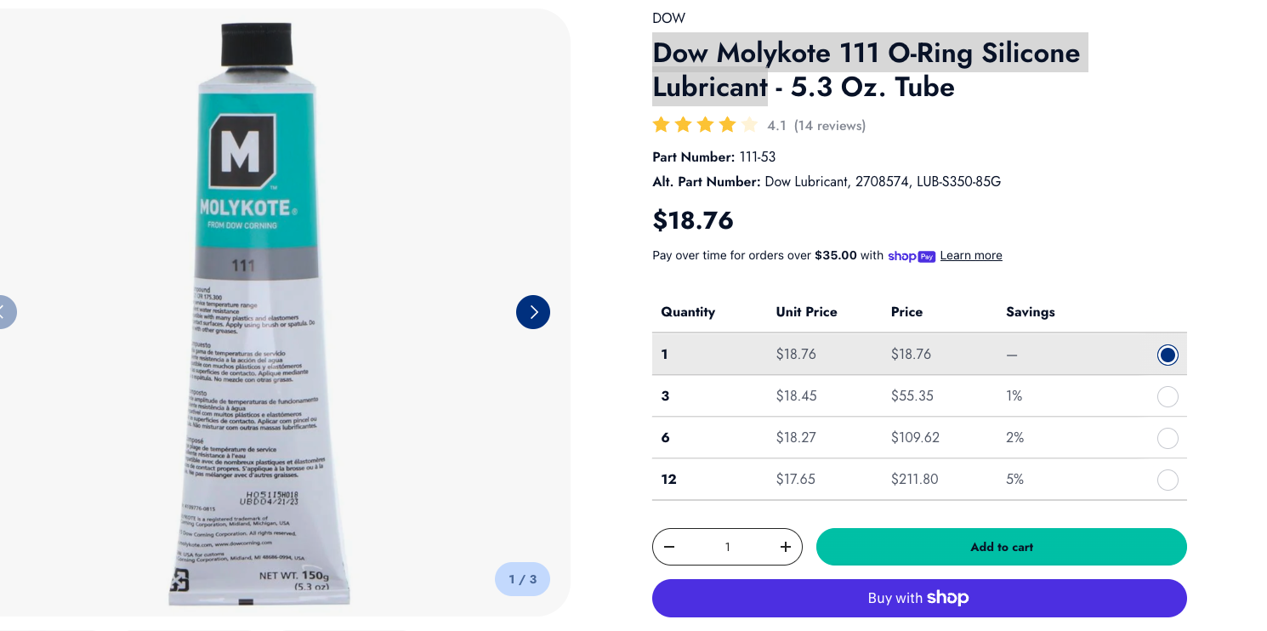
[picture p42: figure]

| Sensor Step 4: Lightly greasing O-rings and IDs of #2 ports | Dow Molykote 111 O-Ring Silicone Lubricant | Molykote Link (https://www.freshwatersystems.com/products/dow-molykote-111-o-ring-silicone-lubricant-5-3-oz-tube?variant=13250411495467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)
| Step 3: Covering top of pressure port hole #8 while filling sensor cup with gear oil | Tape (for covering pressure port during filling) | Electrical Tape (https://www.walmart.com/ip/Hyper-Tough-Electrical-Tape/13709008395?wl13=5073&selectedSellerId=0&wmlspartner=wlpa)

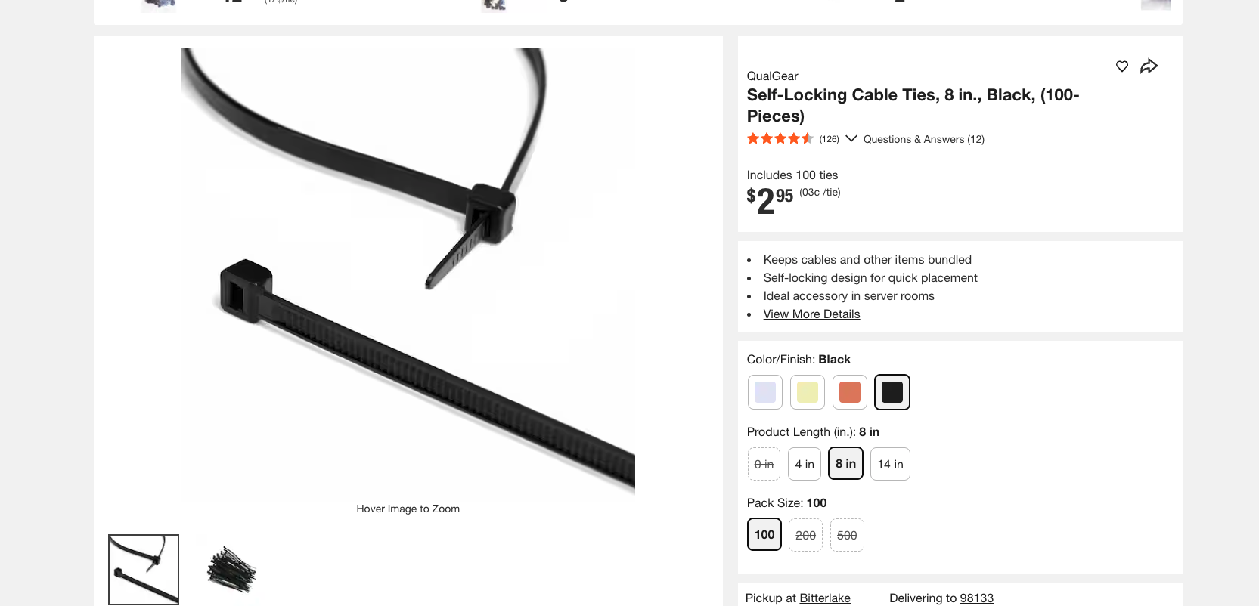
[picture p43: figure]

| Steps 13 & 15: Securing actuator cable at #13 plate exit points | Zip Ties (MMC# 7130K13) | Zip Ties (https://www.homedepot.com/p/QualGear-Self-Locking-Cable-Ties-8-in-Black-100-Pieces-CT5-B-100-P/303357779?locale=en-US&fp=ggl)

Outer Assembly Installation tool + Adhesives and Consumables

Step Used | Description | Vendor Link | Image
3, 4, 8, 13 | Loctite 425 Threadlocker | Loctite threadlocker (https://www.uline.com/Product/Detail/S-26380/Loctite-Adhesives/Loctite-Instant-Adhesive-425-Assure?pricode=WB0948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)
5, 11 | Dow Molykote 111 O-Ring Silicone Lubricant | Molykote Link (https://www.freshwatersystems.com/products/dow-molykote-111-o-ring-silicone-lubricant-5-3-oz-tube?variant=13250411495467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)
2, 6 | Aqua Shield Waterproof Grease | Aqua Shield (https://www.qcsupply.com/products/stenner-aquashield-5-5-oz?variant=51003288256819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)
7, 13 | 3mm Hex Drive Screwdriver | 3 mm Hex (https://www.digikey.com/en/products/detail/wiha/36730/511075?gclsrc=aw.ds&gad_source=1&gad_campaignid=20232005509&gbraid=0AAAAADrbLlgR33g_0IEcxBuh_0exNC-bO)

Endcap Assembly

Step Used | Description | Vendor Link | Image Link

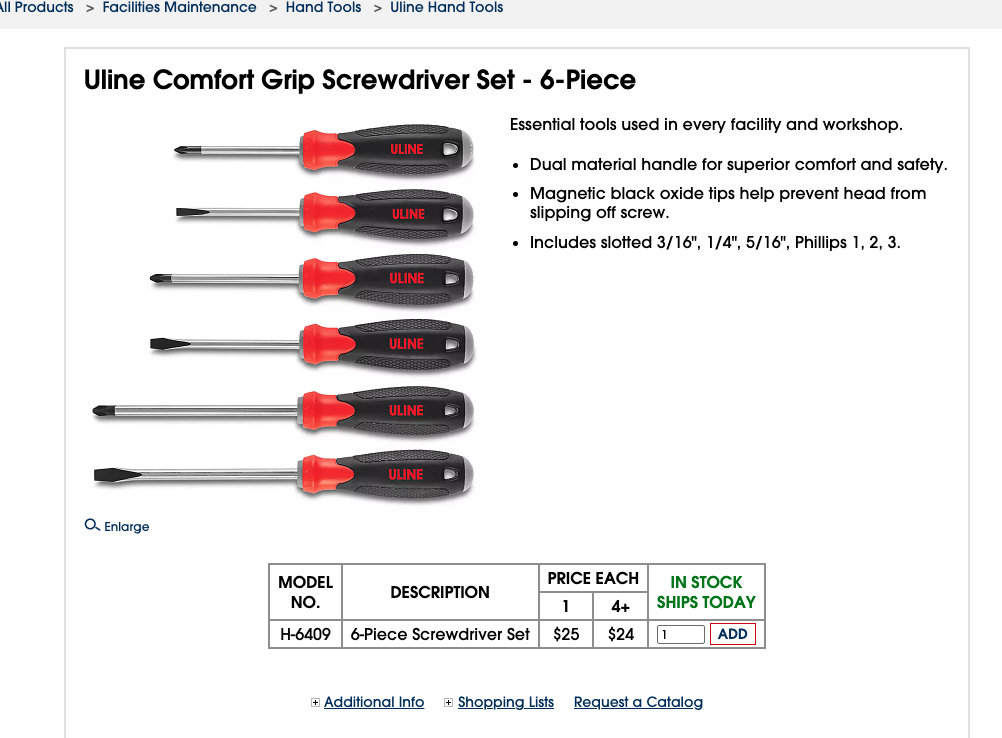
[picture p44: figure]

1, 4, Pushing in retaining rings, | Flathead screwdriver(3-6/16”) Any tool that can help push retaining rings in. | Flathead Screwdriver (https://www.uline.com/Product/Detail/H-6409/Hand-Tools/Uline-Comfort-Grip-Screwdriver-Set-6-Piece?pricode=WB0016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)
4 | Dow Molykote 111 O-Ring Silicone Lubricant | Molykote Link (https://www.freshwatersystems.com/products/dow-molykote-111-o-ring-silicone-lubricant-5-3-oz-tube?variant=13250411495467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)
5 | Loctite 425 Threadlocker | Loctite threadlocker (https://www.uline.com/Product/Detail/S-26380/Loctite-Adhesives/Loctite-Instant-Adhesive-425-Assure?pricode=WB0948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)

# Inner Assembly

# Inner Assembly

a. Unscrew the rod end of the actuator if still attached shown in Figure 1. Make sure to not unscrew the actuator rod.

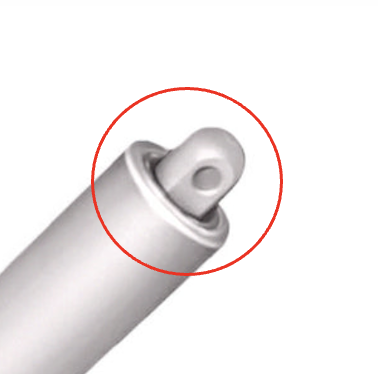
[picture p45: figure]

Figure 1. The rod end is circled in red.

a. Lightly coat LCP Actuator mount (#36) with vibratight threadlocker (T5), wait at least 15 mins
b. Screw into the Actuator (#4). Double check the #4’s rod is fully screwed into the actuator.
3. Lightly grease Hydraulic seal (#45) and install onto LCP Piston #1 (part #3)
  a. #45 is the bigger one
  b. The O-ring goes towards pressure
    i. Pressure is coming from the outside
    ii. Rounded end is the pressure end
4. Lightly grease Hydraulic seal (#46 ) and insert into LCP piston #1
  a. #46 goes in the top groove
  b. O-ring up
5. Clean #25 threads with IPA and grease with Vibratight threadlocker, attach LCP Actuator to LCP Piston #2 with #25.
6. Install Wear Ring #42 into LCP Piston #1 (part #3)
7. Using Aquashield, generously grease the inner bore of LCP Piston #1 (part #3) and the outside diameter of LCP Piston #2 (part #5)
8. Install Piston 2 installation tool, 000574, onto LCP Piston #2 (part #5)
9. Install wear ring (#44) onto LCP Piston #2 (part #5) so that the ends of #44 are aligned with LCP Piston #2s wire clearance.
10. Insert LCP Piston #2 (part #5) into LCP Piston #1 (part #3)
  a. Can use a pair of needle nose pliers to gently pull on the end of #44 during installation
  b. After installation move actuator cable to the inside of the wear ring
11. Remove Piston installation tool 00574
12. Pass the #4 actuator’s cable through the lower LCP Gas Spring Ring (#13) using one of the gas spring mounting holes located 90 degrees from the ear cutouts
  a. Add a photo of the ear cut outs
13. Make sure LCP Piston #2 - (part #5) is fully extended in LCP Piston #1 - (part #3),
a. Fully seat #13 in LCP Piston #1(a rim will prevent it from going further), pull the cable tight and mark where it exits the top of #13.
b. Remove #13, then measure 1" from mark on cable towards the end of where the wire ends
c. Install a zip tie around the cable (MMC#7130K13), tight enough that it does not move on the cable.
14. Retract piston #5 and install lower #13 as shown into #3
  a. Mark location of # 13 gas spring ear cutouts on #3’s ID so they align with the 2 counterbored slots in the top of #5
  b. Fully extend piston #5
  c. Secure #13 to #3 with 100mm Steel Internal Retaining Ring (#7) so the free ends are 180 degrees from the actuator cable
15. Add a second ziptie around the cable ~ 0.25" above where cable exits #13’s plate.
16. 2X: Bolt Gas Spring #6 to Upper #13 as shown with Nylon-Insert Locknut (#17)
a. Apply Vibratight threadlocker to the threads of four #15 fasteners. Allow the threadlocker to cure for a minimum of 15 minutes.
b. Install washer #16 onto each fastener and pass all four assemblies through the upper #13 plates.
18. 2X: Pass Steel Socket Head Screw (#15) through LCP Gas Spring Spacer (#26)`
  a. Place on opposite sides from each other
19. Lower Battery Installation:
a. CRITICAL: Verify that the free ends of the two #6 gas springs are properly aligned with the two counterbored slots in component #5 before proceeding. As shown in Fig X.

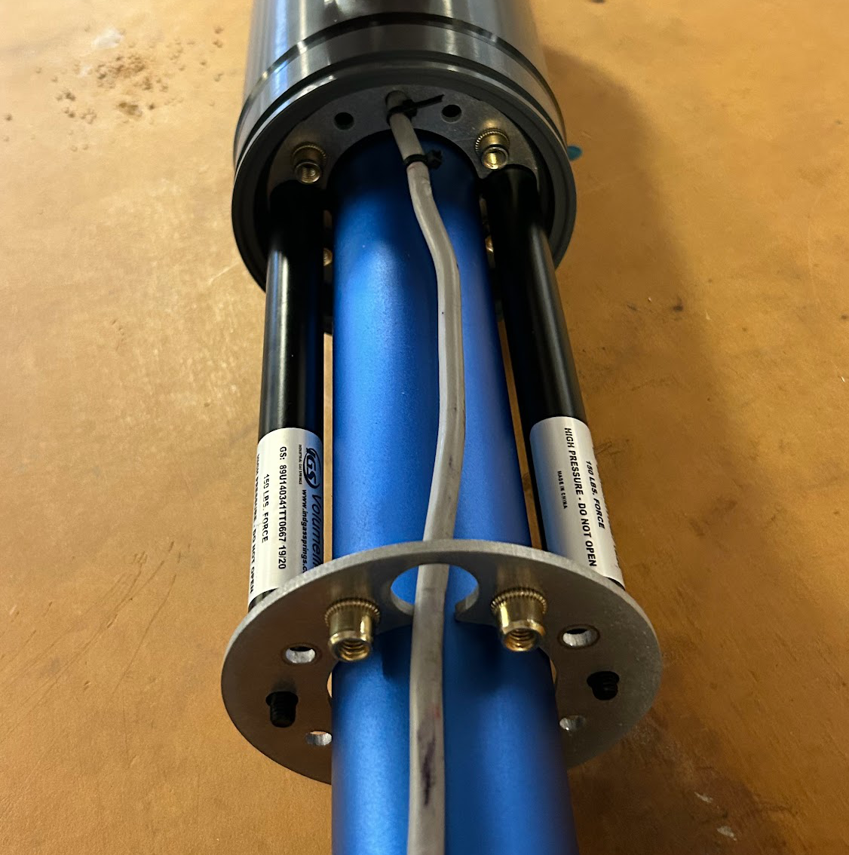
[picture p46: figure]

Fig x. Pistons aligned inside of counterbored holes.

b. Battery Carriage Installation: Attach the 4 battery packs to the 3D printed battery holders(#X) shown in Fig X.

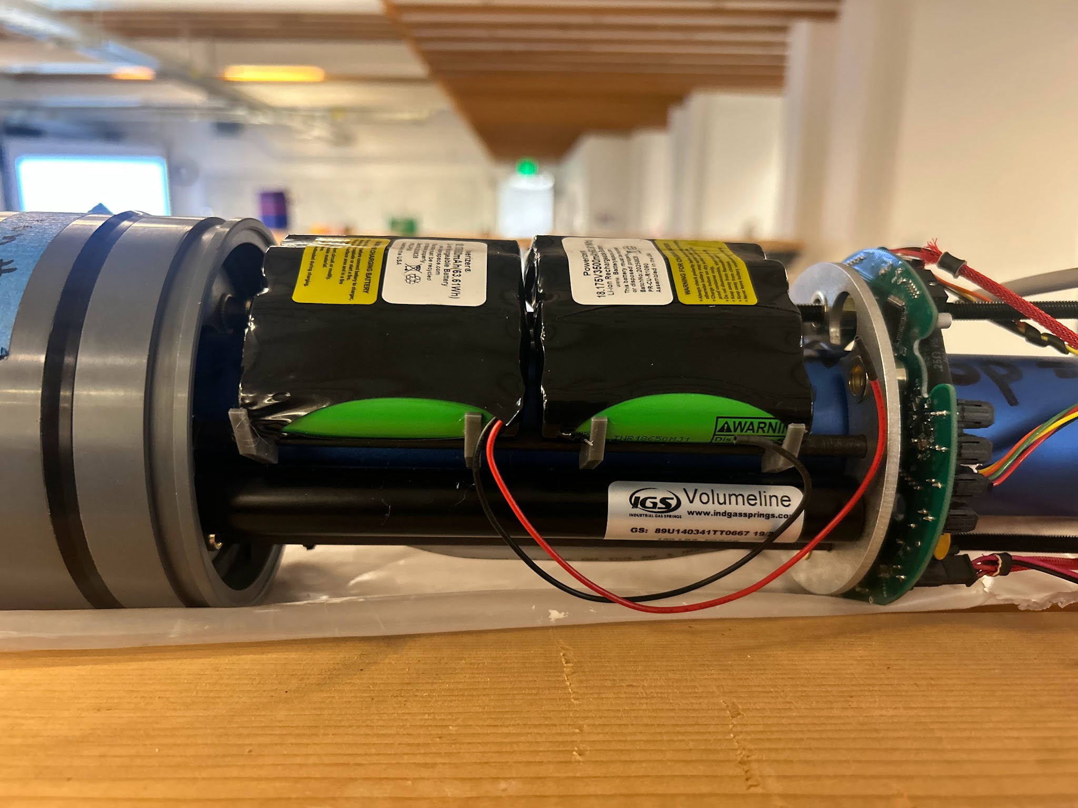
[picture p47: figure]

Fig X. Batteries mounted on 3D printed parts.

20. Critical

# Outer Assembly

# Outer Assembly:

1. Extend the actuator all the way out.

2. Generously coat inside of housing #1 up ~10" from non cross drilled end, and Internal Assembly Piston1 OD, including piston seal, with Aqua Shield grease.

3. Install Piston1 Installation Tool Assembly, 500152, around housing #1.

4. Install wear ring #43 into piston #4, hold in place with your fingers.

5. Insert Inner Assembly half way into housing #1, in the side opposite the end cap cross drilled retaining holes.

6. Remove Piston1 Installation Tool Assembly, 500152.

7. Fully insert Inner Assembly into housing #1.

8. Lightly coat #36 with Vibratight threadlocker and wait 15+min.

9. Screw Endcap Assembly #2 onto #36 until it bottoms out.

10. Rotate housing #1 until endcap retaining holes line up with the cross tapped holes in the endcap (May need to use a strap wrench).

11. Coat #2 sealing O-ring and the first ~1" of the ID of Housing #1 with Dow Corning Silicone #4 grease.

12. Command the actuator to retract ~9". As the actuator retracts, guide the endcap#2 into housing #1.

13. 2X: Put a drop of Loctite Threadlocker 425 onto #31. Install Endcap retaining screws, #31 w/ #4 until #41 is fully compressed. Be careful not to overtighten.

14. Slide first #21, as shown over Piston2.

15. Lay #29 into the groove in #21, hold in place while you install 2nd #21 over the end of Piston2.

16. Secure in place with #20.

17. Fully retract actuator.

18. Run diagnostics tests and put instrument into storage mode.

# Sensor Cap Assembly

# Sensor Endcap Installation Instructions:

1. #10 and #54 insertion into Endcap
a. If not already installed, insert #54 into #10
b. Smear a light layer of Molykote(O-ring grease) into the O-ring indent of #10(the larger gap)
c. Insert O-ring #38 into the greased gap, and insert into endcap hole #5, push #10 so that it is flush with the top of the endcap
d. Insert metal retaining ring on #10 on the inner side of the endcap,(example in photos below.
2. #8 Endcap Installation
a. Smear a light layer of Molykote(O-ring grease) in the larger indent of #8
b. Insert O-ring #38 into the greased gap, and insert into endcap hole #4, push #8 so that it is flush with the top of the endcap
c. Insert metal retaining ring on #8 on the inner side of the endcap,(Figure 1&2)
3. #11 Endcap installation
a. Smear a light layer of Molykote(O-ring grease) in the larger indent of #11
b. Insert O-ring #38 into the greased gap, and insert into endcap hole #2, push #11 so that it is flush with the top of the endcap(it may not be completely flush.
c. Insert metal retaining ring on #11 on the inner side of the endcap(Figure 1.)
d. Insert power wires and communications wires into #28
e. Insert #28 into #11, the top of #28 should sit below the threaded inner lining of #11 shown in Figure 3.
f. To Seal, screw in the bolt shown in Figure 4.
4. #30 Antenna housing endcap installation
a. Wrap #32 in foam and tape to keep in place
b. Insert #32 into #30, with the foam attached.
c. Insert into hole #1 of endcap and push flush with the top of the endcap
d. Secure with #33 retaining ring

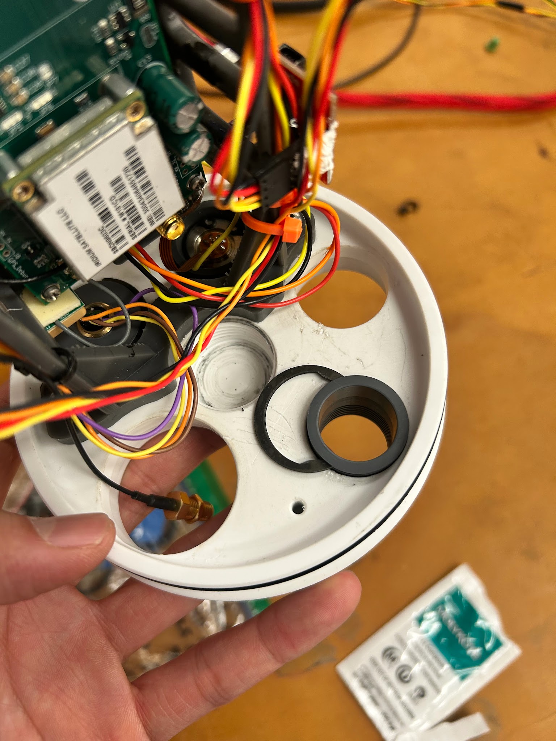
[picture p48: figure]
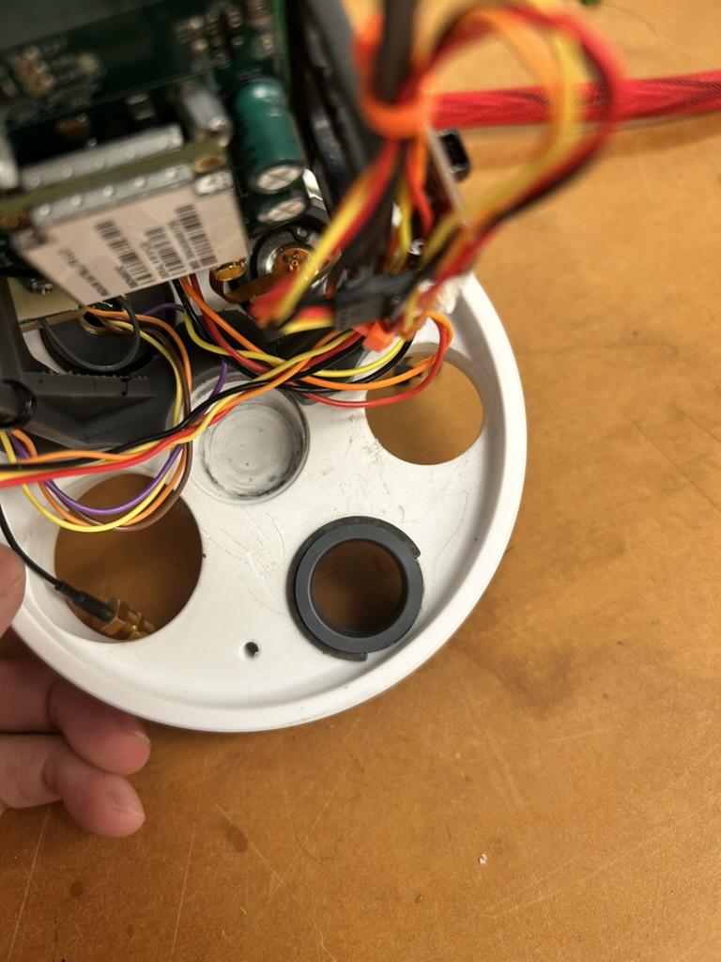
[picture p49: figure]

Figure 1 and 2. Retaining ring installation

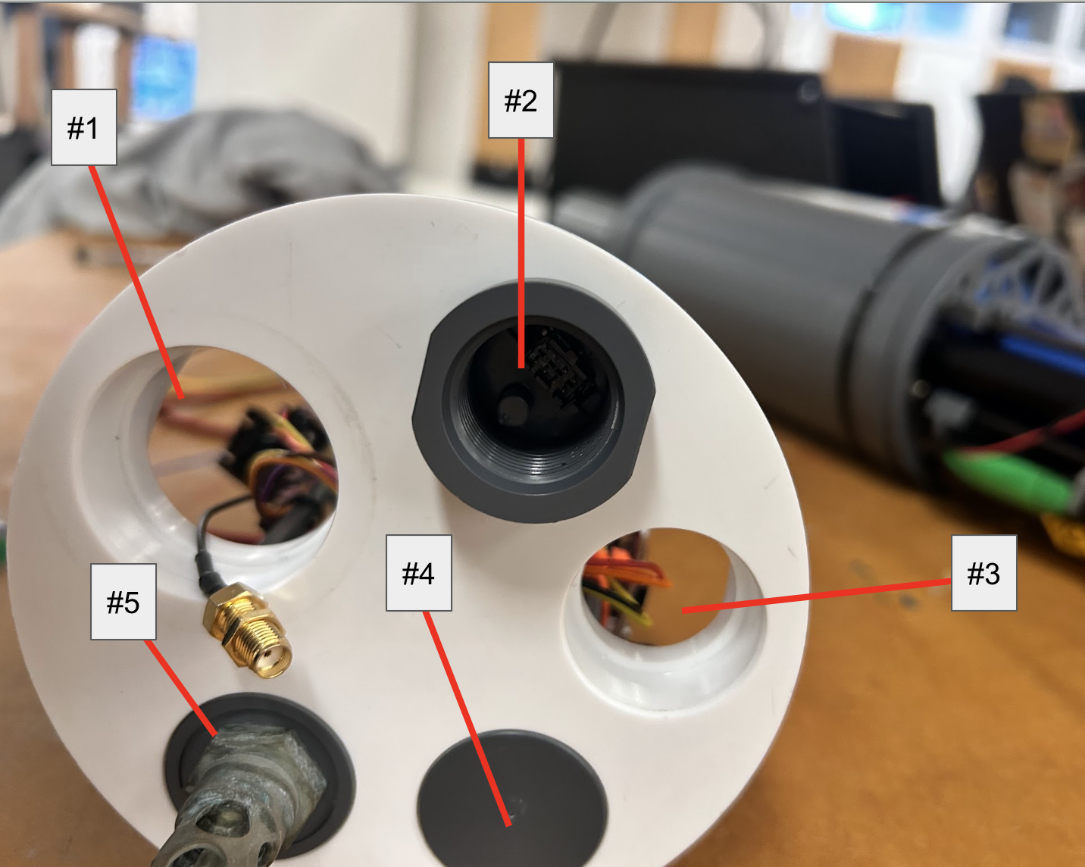
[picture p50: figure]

Figure 3. Endcap hole labels.

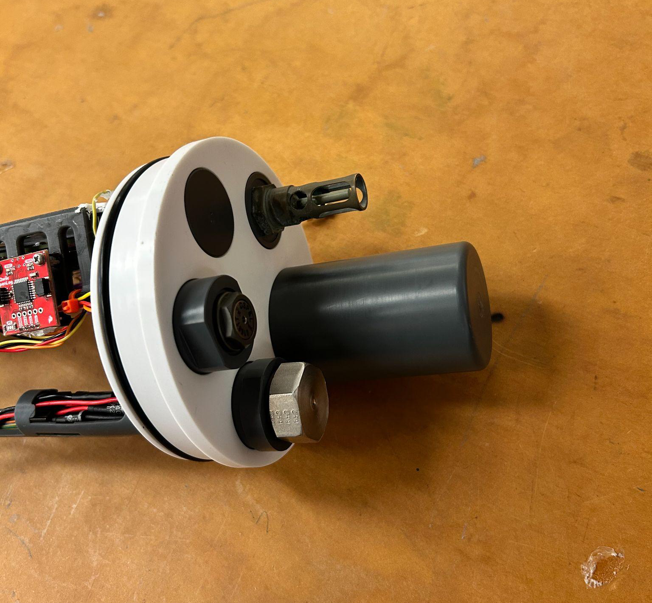
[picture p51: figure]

Figure 4. Metal screw cap for power and comms

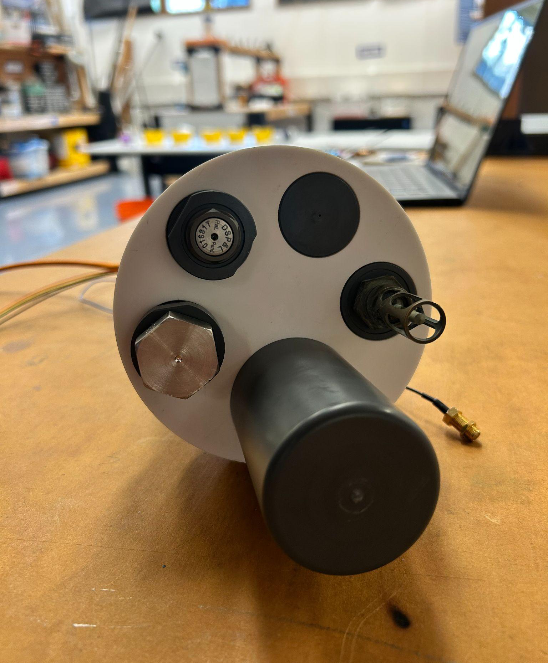
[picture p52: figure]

Figure 5. The completed endcap.

# Flashing the Control Board

# Flashing the Control Board

Please follow the instructions in the LCP quick start document under firmware flash. You use the segger j-link flashing tool to flash the new firmware onto the LCP control board, after you make the configuration and artemis debug.h file changes and save them. You can then use the TTL to usb board and teraterm to monitor the output of the control board, but you cannot send commands to the control board. Everytime you re-apply power the LCP will restart per the settings in the configuration file, and will then profile until it either runs out of power, or you reach the number of profiles set in the config.h file.

Note: After flashing with the J-link remove the J-link cable and power off the LCP. Then resupply power and hit the reset button/switch, this will start the LCP with the correct profile.

https://github.com/NOAA-PMEL/EDD-LCP_Control/blob/Ver1.0/LCP%20Quick%20Start%20Guide_v0.pdf (https://urldefense.com/v3/__https://github.com/NOAA-PMEL/EDD-LCP_Control/blob/Ver1.0/LCP*20Quick*20Start*20Guide_v0.pdf__;JSUl!!K-Hz7m0Vt54!mmd97fwyskiMo8CLv8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)

# Git Hub Links

Git Hub Links

- NOAA-PMEL/NOAA-PMEL-Low-Cost-Profiler: NOAA PMEL's Low Cost Profiler Opensource hardware and Software Repository (https://github.com/NOAA-PMEL/NOAA-PMEL-Low-Cost-Profiler)

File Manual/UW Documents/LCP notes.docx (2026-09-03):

Notes: ask Sasha about Solidworks access.

Build up documentation to be accessible without Solidworks

Changing these files to a more accessible file type will allow people with a more affordable cad program to open and print with 3d printing etc.

1. Open your SolidWorks file
2. Go to File > Save As
3. In the "Save as type" dropdown, select your desired format:

Common Export Options:

- **STEP (.step, .stp) - Best for 3D models
- **IGES (.igs, .iges) - Alternative 3D format
- DXF (*.dxf) - Good for 2D drawings
- DWG (*.dwg) - AutoCAD format
- STL (*.stl) - For 3D printing
- **Parasolid (.x_t, .x_b) - High-quality 3D
- ACIS (*.sat) - Another 3D option
4. Click Options to adjust export settings if needed
5. Click Save
- Convert SLDPRT files for circuitry to more accessible files like GRB (Gerber files)

Things to think about:

- how can we make diagrams or images of circuits more uniform and easy to reference compared to OPEN CTD
- Creating a software repository with a readme and documentation
- Create a data conversion document, R or Excel
- Link documentation for support of sensors boards microcontrollers
- Expanding the read me to applications, purpose of os, motivation, basic op systems used.
- Code

Open source projects

- Bristlemouth
- OpenCTD
- OpenDrift
  - Modeling for where things go in ocean/ atmosphere

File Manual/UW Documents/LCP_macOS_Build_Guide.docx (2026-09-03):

LCP macOS Build Guide

Toolchain setup and build instructions for macOS

# Hardware Required

- Tag Connect Plug o'nails: TC2030-CTX
- SEGGER J-Link EDU Mini V2
- USB to TTL serial adapter: FT232RL

# Step 1: Install Homebrew

Homebrew is the package manager used to install most of the required tools. Open Terminal (Cmd+Space, type Terminal) and run:

/bin/bash -c "$(curl -fsSL https://raw.githubusercontent.com/Homebrew/install/HEAD/install.sh)"

# Step 2: Install Toolchain

Run the following commands in Terminal:

brew install cmake ninja

brew install --cask gcc-arm-embedded

brew install --cask segger-jlink

Install Visual Studio Code:

- Download from: https://code.visualstudio.com/
- Or via Homebrew:
  - brew install --cask visual-studio-code

# Step 3: Set Up System PATH

Homebrew-installed tools (cmake, ninja, arm-none-eabi-gcc) are added to PATH automatically. J-Link must be added manually.

## Find your J-Link version

Run the following to see what is installed:

ls /Applications/SEGGER/

You should see a folder like JLink_V942. Use that folder name in the next step.

## Add J-Link to PATH

Replace JLink_V942 with your actual version if different:

echo 'export PATH="/Applications/SEGGER/JLink_V942:$PATH"' >> ~/.zshrc

source ~/.zshrc

## Create JLink.exe symlink

The build system looks for JLink.exe (the Windows name). Create a symlink so it resolves correctly on Mac:

sudo ln -s /Applications/SEGGER/JLink_V942/JLinkExe /usr/local/bin/JLink.exe

Note: Replace JLink_V942 with your actual version. You will be prompted for your Mac password.

## Verify all tools are accessible

arm-none-eabi-gcc --version

cmake --version

ninja --version

JLinkExe --version

Each command should print a version number. If any return 'command not found', the PATH is not set correctly.

# Step 4: Clone Required Repositories

## AmbiqSuite SDK

Clone the AmbiqSuite SDK into your project folder (adjust path as needed):

git clone https://github.com/sparkfun/AmbiqSuiteSDK ~/Downloads/LCP/AmbiqSuiteSDK

Note: The folder must be named exactly AmbiqSuiteSDK — CMake looks for this name. If cloned with a different name, rename it with: mv <old-name> AmbiqSuiteSDK

## EDD-LCP_Control Firmware

Clone the Ver1.0 branch of the firmware repository:

git clone --branch Ver1.0 https://github.com/NOAA-PMEL/EDD-LCP_Control.git ~/Downloads/LCP/EDD-LCP_Control

⚠ Do not include angle brackets < > around the URL. The command above is complete as written.

# Step 5: Build the Firmware

## Navigate to the firmware directory

cd ~/Downloads/LCP/EDD-LCP_Control/Firmware/LCP_Control

## Create and enter the build directory

mkdir build

cd build

## Run CMake

cmake .. -DCMAKE_TOOLCHAIN_FILE="../arm-gcc-toolchain.cmake" -G "Ninja"

Expected output includes:

- Using Ambiq Suite SDK Path: .../AmbiqSuiteSDK
- Configuring done / Generating done

Note: A warning about JLink.exe not found is expected and harmless if the symlink from Step 3 was created. CMake will still configure correctly.

## Flash the firmware

With the J-Link connected, board powered on, and Tag Connect seated on the board:

ninja flash_jlink

## Alternative flash (RS232 to TTL)

Only works when there is no error state on the control board (i.e. not the first flash, and the logger has correct pressure profiles):

ninja bootload_asb

# Step 6: Rebuilding After Config Changes

When making changes to config.h, delete the build directory and repeat the build steps:

cd ~/Downloads/LCP/EDD-LCP_Control/Firmware/LCP_Control

rm -rf build

mkdir build && cd build

cmake .. -DCMAKE_TOOLCHAIN_FILE="../arm-gcc-toolchain.cmake" -G "Ninja"

ninja flash_jlink

# Serial Terminal (TeraTerm Equivalent)

TeraTerm is Windows-only. On macOS, use one of the following:

## screen (built-in, no install needed)

First find your device name after plugging in the FT232RL adapter:

ls /dev/tty.usb*

Then connect at 921600 baud for the Quick Start procedure:

screen /dev/tty.usbserial-XXXX 921600

To exit screen: press Ctrl+A, then Ctrl+\, then confirm with 'y'.

Note: For the Firmware Flash procedure (piston board), use baud rate 115200 instead.

## CoolTerm (free GUI app)

- Download from https://freeware.the-meiers.org/
- Set baud rate to 921600
- Set line ending to LF only (Options > Terminal > Enter Key Emulation: LF)
- Enable logging via Connection > Capture to Text File

# Troubleshooting

## CMake error: Ambiq Suite SDK path not found

The AmbiqSuiteSDK folder is missing or misnamed. Verify it exists:

ls ~/Downloads/LCP/

If the folder is named differently (e.g. AmbiqSuiteSDK-main), rename it:

mv ~/Downloads/LCP/AmbiqSuiteSDK-main ~/Downloads/LCP/AmbiqSuiteSDK

## CMake warning: JLink.exe not found

This warning is expected on Mac. As long as the symlink from Step 3 was created correctly, ninja flash_jlink will still work. Verify with:

which JLink.exe

Should return /usr/local/bin/JLink.exe. If not, re-run the symlink command from Step 3.

## ninja flash_jlink: Cannot connect to the probe/programmer

The firmware compiled successfully but J-Link cannot reach the hardware. Check:

- J-Link EDU Mini is plugged into USB
- Board is powered on
- Tag Connect TC2030-CTX is fully seated on the board header

For more detail on the connection failure, run:

JLinkExe -device AMA3B1KK-KBR -if SWD -speed 4000

## git clone: zsh parse error near newline

You included angle brackets around the URL. Remove them — the URL should be pasted directly with no surrounding characters:

git clone --branch Ver1.0 https://github.com/NOAA-PMEL/EDD-LCP_Control.git

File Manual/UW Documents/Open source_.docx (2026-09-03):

# Manual

Windows login

Username: LCP_student@outlook.com

PW: Float_and_Sink

Github links:

NOAA-PMEL/NOAA-PMEL-Low-Cost-Profiler: NOAA PMEL's Low Cost Profiler (https://github.com/NOAA-PMEL/NOAA-PMEL-Low-Cost-Profiler)

NOAA-PMEL/EDD-LCP_Control (https://github.com/NOAA-PMEL/EDD-LCP_Control/blob/Ver1.0/LCP%20Windows%20Build%20Guide.docx)

12-28 v

20-27 v ideal

Dont go below 20 or above 28 volts

Redesign of battery charging

Wiring diagrams will be insufficient

Chat with Katie:

Chris Roman URI

- Propeller

There is an example of wiring

Connectors (Molex)

There is piston greases

Will go everywhere

Sharpie marks on the ram (90 degree marks)

Will help in aligning the gas springs

The height measurement of 6.46 inches is very important

Snap ring should be oriented with the opening perpendicular to gas spring ears

We have gen zero electronics

Do not write documentation about it

Boards have to be fully wired/connected before power is applied

Power on batteries are not plugged in

Put diodes into the battery pack in the alkaline battery packs

Be very careful about battery connected vs power not connected

No salinity sensor

Only pressure and temperature

When everything is put together before the end cap you extend the ram all the way and then take the outer tube and slide it on until about an inch left and then screw the end cap on. Screw the outer thing until the screw ports are aligned. Then decrease the ram piston. Make sure you have a way to talk to the ram and that it has power.

MAKE SURE THE RAM HAS POWER AND COMS BEFORE FULLY CLOSING

Run it on the bench with out the outer shell for testing

# Chats with people

# Help resources:

Zack Johnson - SOFAR

Essentially want to be a plug and play like bristlemouth, a base interface that users can add whatever sensors that they want, they could also change the code to change the mission type to capture whatever depth range they want.

Finding community leads?

How to go from user to contributor?

How do contributors differ?

Should there be sort of an admin style approach with firmware/mech/electrical?

How did you approach building up a user base? Obviously SOFAR/Bristlemouth is more of a product, but outside of the product itself how did you sell bristlemouth?

How have you seen the bristlemouth product be modified and used?

Creating an organization on github

Place to start:

- How imagine people getting/building
- Things they need to know to be successful
- From scratch?
- Tailoring licenses/repos
- Machining expertise
- Does it matter if commercial not commercial
- Creative commons mit/apache
- How would people acquire the materials
- Documentation
- Where people interface the most
- Dont worry bout the licensing too much

Initial steps;

- Reached out to people who wanted to work of the platform
- Support small group
- Reasonable know how
- Very specific use cases free hardware

Already had community built from openrov

Find that community

Oceanography for everyone

Webinar

How to market

Use the UW community

Maker community

Fin the Unis that highest likelihood of doing something

Forum: Discourse

Elevate people to admin

Managing a big space like that

Speak with folks at blue robotics

How much should be user to user solution

Github is good for some things

But not as ubiquitous as discourse

Just having a hands off place for users

Trevor Harrison - APL

Qs:

What type of research questions would you be able to answer with this product.

- Salinity, temp, pressure
- DO, acoustic
- Mixed layer, coastal processes
- River plumes, tidally influenced, or just the mixing
- Sounds speed gradients
- DO lvls
- Passive Acoustics monitoring
- Scripps AUEs - PAR
- Turbidity
- Carbon capture and storage
- Camera
- Water qual measurements

Understanding how the addition of sensors will effect ballasting

How sensors will effect the float

What type of sensors would you want to include/add

If you were to use this product, what would you need in terms of technical documentation/how much would you need manufactured.

- Instruction manual - lego steps
- Steps- logical subsystems
- Troubleshooting guide issues and how to address them
- Well documented code base
- What power levels, what com channels are open, control of buoyancy based off of the new sensors
- Acccsessing sensor information and output of buoyancy engine
- mass , volume, of base model
- Volume of the buoyancy engine
- Change in displaced volume as a function of motor input
- For base user make it so easy to use like a phone
- Hs lvl understanding of sci and tech
- Assume people have basics
- Having the tool needs
- Or make to order
- Xometry
- Send cut send
- Ashcut
- Build manual, startup/, operational, and trouble shooting, data offload and analysis

Baseline for the sensors

Creating the community, minimizing the number of channels

Do you have past experience with open source projects, what worked what didn’t?

Good documentation eg.

https://community.particle.io/

Chat with Andrew Thaler:

Finding community leads?

How to go from user to contributor?

How do contributors differ?

Should there be sort of an admin style approach with firmware/mech/electrical?

How did you approach building up a user base?

Camera traps

Atlas standards

DO/pH

Integrated niskin,

Cool alterations from the community,

Make sure all on board

As:

Make sure good with rules

Not as much documentation, licenses, make sure the tools are open source

Having the software available

Have the WHY for its open source

Limitations for it if its community let it be fully open source

Documentation

Instruction for building it

Monetize it?

Or Preclude it to be a tool for the global community

Software or just hardware

Having the custom parts

Main branch of opentctd softawwre

Some people that can approve

Core founders are the ones with admin control

Personal connections

Presentations at conferences

Collabs for grants

Grand perspective 40-50,

not/to - Centralized data portal

Having that data be autonomous or centralized probably centralized due to satellite,

Ashley Howard chat

- What exactly type of research do you do how would you apply the float
- For glacial fjord flat top can accumulate sediment
- firmware , having several different missions,
- Velocity profiles
- Acoustic modems for tracking
- Isopycnal mode
- Move in 3d langrangian way with the water mass
- Lowers the stakes of science can deploy in more risky
- Glacial fjord
- Gps was a limiting factor due to poor signal with the glacier walls
- Having the horizontal stuff is helpful
- Troubleshooting

Kendall Fonetnot

https://github.com/tedlanghorst/OpenOBS-328

https://tedlanghorst.github.io/OpenOBS-328/about/

https://github.com/tedlanghorst/OpenOBS-328/tree/main/sensor/hardware/3D_print/custom_pcbs

\https://www.nature.com/articles/s44221-023-00124-2

Caiti Guerin

- Lay everything out!
  - Write down what you are making assumptions about
  - Note what needs to change
- Print out all of the manuals
- Label all parts with tape that make sense
- Ask for torque specs
- Lay out all tools before assembly
- Make sure you have everything
- Can set out plywood and move everything
- Try to think about what makes sense
  - Something not specified and two spots could join
  - Missing o-rings
  - What is going where
    - Seals
- Check wires for nicks
- Make sure connectors are good
- Inspect solder joints
- Layout pieces and make sure the thing matches the visuals
- Lock type
  - What is securing what

Robby

- Add that you need to download the installer instead of the .zip for Cmake
- The git hub was missing one of the documents
  - /arm-gcc-toolchain.cmake”
- The run script has something that only works on Linux and it was needed for the set up of windows
- The windows set up needs something that only runs on linux
- AmbiqSuiteSDK only works on linux

# Notes while making

Part 1

- Need to make it more clear that you should start with internal assembly
- Where connection points for actuator are
- Wire stripping and attaching connectors
  - If you want wires twisted
- What parts to use for this connection
- How much wire to cut from actuator, tools required(leave 2inches of inner wires

Part 2: Downloading software for quick start up

Step 1: Follow instructions in this document

- https://github.com/NOAA-PMEL/EDD-LCP_Control/blob/Ver1.0/LCP%20Windows%20Build%20Guide.docx
- Make sure that the paths on your pc are set to the ones specified in the document.
- Check on the version of the downloads
- You can change the path of the downloads of these softwares by using Eg. set PATH=%PATH%;C:\Program Files (x86)\Arm GNU Toolchain arm-none-eabi\14.2 rel1\bin;C:\Tools\ninja-win;C:\Program Files\SEGGER\JLink_V860
- Program files( x86) can be the path on your computer to the download
- Make sure unzip all of the downloaded files
- Windows build is not working rn

Commands to use:

Windows notes:

Make sure the build folder in firmware is deleted if failed

Make sure all the spaces are right in the cmake line

Ver1.0 branch of the edd lcp control github

Terra term for coms

Add instructions for tera term

PuTTY did not work very well for windows

Our max encode max encode= 142432

When using the Actuator it will randomly start extending.

LINUX NOTES:

If git not installed

Use sudo apt install get

If there is a frontend lock then check the current running process of apt and dpkg

If sudo kill does not work

Us sudo rm /var/lib/dpkg/lock-frontend

Sudo rm /var/lib/dpkg/lock

Sudo dpkg –configure -a

Sudo apt install git

This should download git

Use git --version

To make sure that it downloaded

Clone the github NOAA-PMEL/EDD-LCP_Control.git

Error can find file in the github am.mcu.apollo.h

Put installation tool cad files into the git hub

Extending the Actuator:

- Connect the piston board usb to computer
- Power and ground to the power at 24v 4 amp
- Connect to Tera term and use the instructions in the guide:
- https://github.com/NOAA-PMEL/EDD-LCP_PistonDriver/blob/Windows_Build/Documentation/Manual/LCP_Pistonboard_User_Manual.pdf

2. Fix wording of lube coating

3. The installation tool goes around piston 1 not housing 1

Steps 3 and 4 might be switched. You can’t put 43 on with the installation tool on

There need to be an instruction to make the inner assembly

#45 is the big one #46 is the smaller

O-ring goes towards pressure

Pressure is coming from the outside

The rounded end is the pressure end

# 46 goes in top groove o-ring up

Install wear rings closer to the end

Dont need anything that says put an installation tool

For Putty add carriage return and line feed

Install both the wear ring and the o-ring before installing #5 into #3

And before aqua lube

Step 14/15 of inner assembly: how can you put a zip tie on the actuator cables and assemble #13 back onto it?

26 is no longer used

Questions and answers

- 16: We only have two of the steel washers. We need four of them. = I have a lot of these.
- 18: We couldn't find it. = Already installed in your end cap
- 23: We are missing one hex nut. We have 3 but need 4. = I have a lot of these.
- 26: We don't know what it is supposed to be. = No longer used.
- 31: We are missing one. We have 2 but need 3. = Already installed on your version (different elect board and 3-D printed mounting, than on the drawing).
- 35: We couldn't find it. = Not needed on the new electronics board version with the 3-D printed board mount.
- 42, 44- 46: We are confused about what/where they are. We might be missing number 44. = these are the wear rings, you will need to cut the wear material you have to the lengths given, let me know if you need more material?

Use these to make edits to the instructions

Zip tie the actuator cable to screw

Need better firmware flashing instructions 🙁

Flashing notes

- Use the EDD-LCP_Control/LCP Quick Start Guide_v0.pdf at Ver1.0 · NOAA-PMEL/EDD-LCP_Control (https://github.com/NOAA-PMEL/EDD-LCP_Control/blob/Ver1.0/LCP%20Quick%20Start%20Guide_v0.pdf)
- Follow the setup instructions
  - Plug the LCP in and get to tera term
    - We don’t need the shell aspect
- Once you are at the point to follow the j-link instructions plug the jlink wire in
  - The usb end should be in the computer
- Make a build directory
  - This should be in firmware -> LCP_Control
- Change the profile you want in

# Cygwin

- To get to drives on the windows side you have to type the whole directory name
  - cd /cygdrive/c/Users/youruser/whereyouwant

# NEW CAD PARTS

Battery Holder and Wire endcap holder:

https://cad.onshape.com/documents/5b9ea33b384a22354a56cc99/w/bb9b9d8c42264703782c920e/e/1995a938ec3e498a63046295?renderMode=0&uiState=69727226cc2c8ec7467052eb

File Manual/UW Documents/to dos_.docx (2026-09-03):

Week 5 - 4/27 (mon)

- Connected power wiring to LCP control board from power supply
- Cmake directory not found while attempting to flash on Makana’s computer
- Ask Noah what is prebuilt for LCP for documentation on wiring
- Labelled wiring

These are in no particular order

- 4/21 - 4/26
  - Documentation
    - Inner assembly documentation
    - Update manual part list
      - Link mechanical drawing from github
- Change parts number for:
  - inner assembly
  - sensor end cap installation
- Windows build guide

General to dos:

- Bench top testing
  - Flashing the firmware / documentation
  - Run full bench profile
  - Run profile without proposed pressure
  - Make sure temp sensor is working
  - Do we have to calibrate?
- Close the LCP
- Vacuum testing
- Pool Testing
- New windows build guide documentation
- Battery passivation
  - Figure out a system for the lithium batteries for de-passivation
  - Onshape cad references: cover (https://cad.onshape.com/documents/389baa3df56af5ac32d41348/w/02fb28ec6f6007b636529ab9/e/70185a8eca9b419ab99529f9?renderMode=0&uiState=69e7c116d3b47ec7ab34c8fe), body (https://cad.onshape.com/documents/d030a3b9e7008b5556566480/w/0ae34f596f02fcb26c59dfb1/e/d730ecf84c152480eb47b290?renderMode=0&uiState=69e7c1373d190b2d0976af8a)

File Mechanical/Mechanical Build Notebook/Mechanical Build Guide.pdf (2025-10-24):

D

B

A

B

C

D

8 | 7 | 6
8 | 7 | 6 | 5 | 4 | 3 | 2 | 1
5 | 4 | 3 | 2 | 1

A

DESCRIPTION

Low Cost Profiler
DRAWN NLS | DATE 6/10/2020
CHECKED | DATE | PRODUCT Low Cost Profiler
DRAWING NUMBER | ASSEMBLY NUMBER | CONFIGURATION Default | REV. A | SHEET OF
DECIMALS | PLOT DATE

C

3 | | | REVISIONS
ZONE | REV. | DESCRIPTION | DATE | APPROVED
| A | | 10/24/2025
ITEM NO. | PART NUMBER | DESCRIPTION | Stock Size | Vendor | Finish | Default/QTY.
1 | 000521 | Low Cost Profiler Housing | BA0450A | Amalga Composites | | 1
2 | 000522 | LCP Instrument Endcap | | | | 1
20 | 91650A490 | 1-3/8" OD, Heavy Duty Spiral External Retaining Ring, 18-8 Stainless Steel | MMC# 91650A490 | McMaster Carr | | 1
21 | 000539 | Low Cost Profiler Brush Drag Plate Retainer | | | | 2
29 | 000546 | Low Cost Profiler Drag Brush | MemFlex Brush, 6mm x 5mm spine, 3.0" trim, 0.020" black level polypro | Memtech Inc. | 9.4" Length | 1
31 | 92290A139 | M4 x 0.7mm Thread, 6mm L, Socket Head Screw | MMC# 92290A139 | McMaster Carr | | 2
36 | 000532 | Low Cost Profiler Actuator Mount | | | | 1
41 | 94241A520 | M4 Split Lock Washer, 4.4mm ID x 7mm OD, 316 Stainless Steel | MMC#94241A520 | McMaster Carr | | 2
Notes: 1. | UNLESS OTHERWISE SPECIFIED | THIRD ANGLE PROJECTION | 7600 Sand Point Wy NE NOAA-PMEL Seattle, WA 98115 206-526-6800 Engineering Division
NO MODIFICATION OF SPECIFIED DIMENSIONS OR MATERIALS IS ALLOWED UNLESS APPROVED BY NOAA ENGINEERS. BREAK SHARP EDGES 0.005 MIN MACHINED FILLETS 0.015 MAX SURFACE FINISH 125 DO NOT SCALE DRAWING | DIMENSIONS ARE IN INCHES TOLERANCES ARE: ANGLES 1 FRACTIONS 1/16 .X 0.05 .XX 0.02 .XXX 0.005

21

21

1

31 2X

41 2X

29

20

36

2

Outer Assembly Installation Instructions:
1. Extend actuator all the way out.
2. Generously coat inside of housing #1 up ~10" from non cross drilled end, and Internal Assembly Piston1 OD, including piston seal, with Aqua Shield grease.
3. Install Piston1 Installation Tool Assembly, 500152, around housing #1.
4. Install wear ring #43 into piston #4, hold in place with your fingers.
5. Insert Inner Assembly half way into housing #1, in the side opposite the end cap cross drilled retaining holes.
6. Remove Piston1 Installation Tool Assembly, 500152.
7. Fully insert Inner Assembly into housing #1.
8. Lightly coat #36 with Vibratight threadlocker and wait 15+min.
9. Screw Endcap Assembly #2 onto #36 until it bottoms out.
10. Rotate housing #1 until endcap retaining holes line up with the cross tapped holes in the endcap (May need to use a strap wrench).
11. Coat #2 sealing O-ring and the first ~1" of the ID of Housing #1 with Dow Corning Silicone #4 grease.
12. Command the actuator to retract ~9". As the actuator retracts, guide the endcap#2 into housing #1.
13. 2X: Put a drop of Loctite Threadlocker 425 onto #31. Install Endcap retaining screws, #31 w/ #4
until #41 is fully compressed. Be careful
not to overtighten.
14. Slide first #21, as shown over Piston2.
15. Lay #29 into the groove in #21,
hold in place while you install
2nd #21 over the end of Piston2.
16. Secure in place with #20.
17. Fully retract actuator.
18. Run diagnostics tests and
put instrument
into storage mode.

Installation Tools Required:
1. Piston1 Installation Tool Assembly, 500152
2. Vibratight VC-3 Threadlocker
3. Loctite 425 Threadlocker
4. Dow Corning #4 Silicone Grease
5. Aqua Shield Waterproof lithium based grease
6. 3mm hex drive screwdriver.
7. Strap wrench

35

9.4

4.9

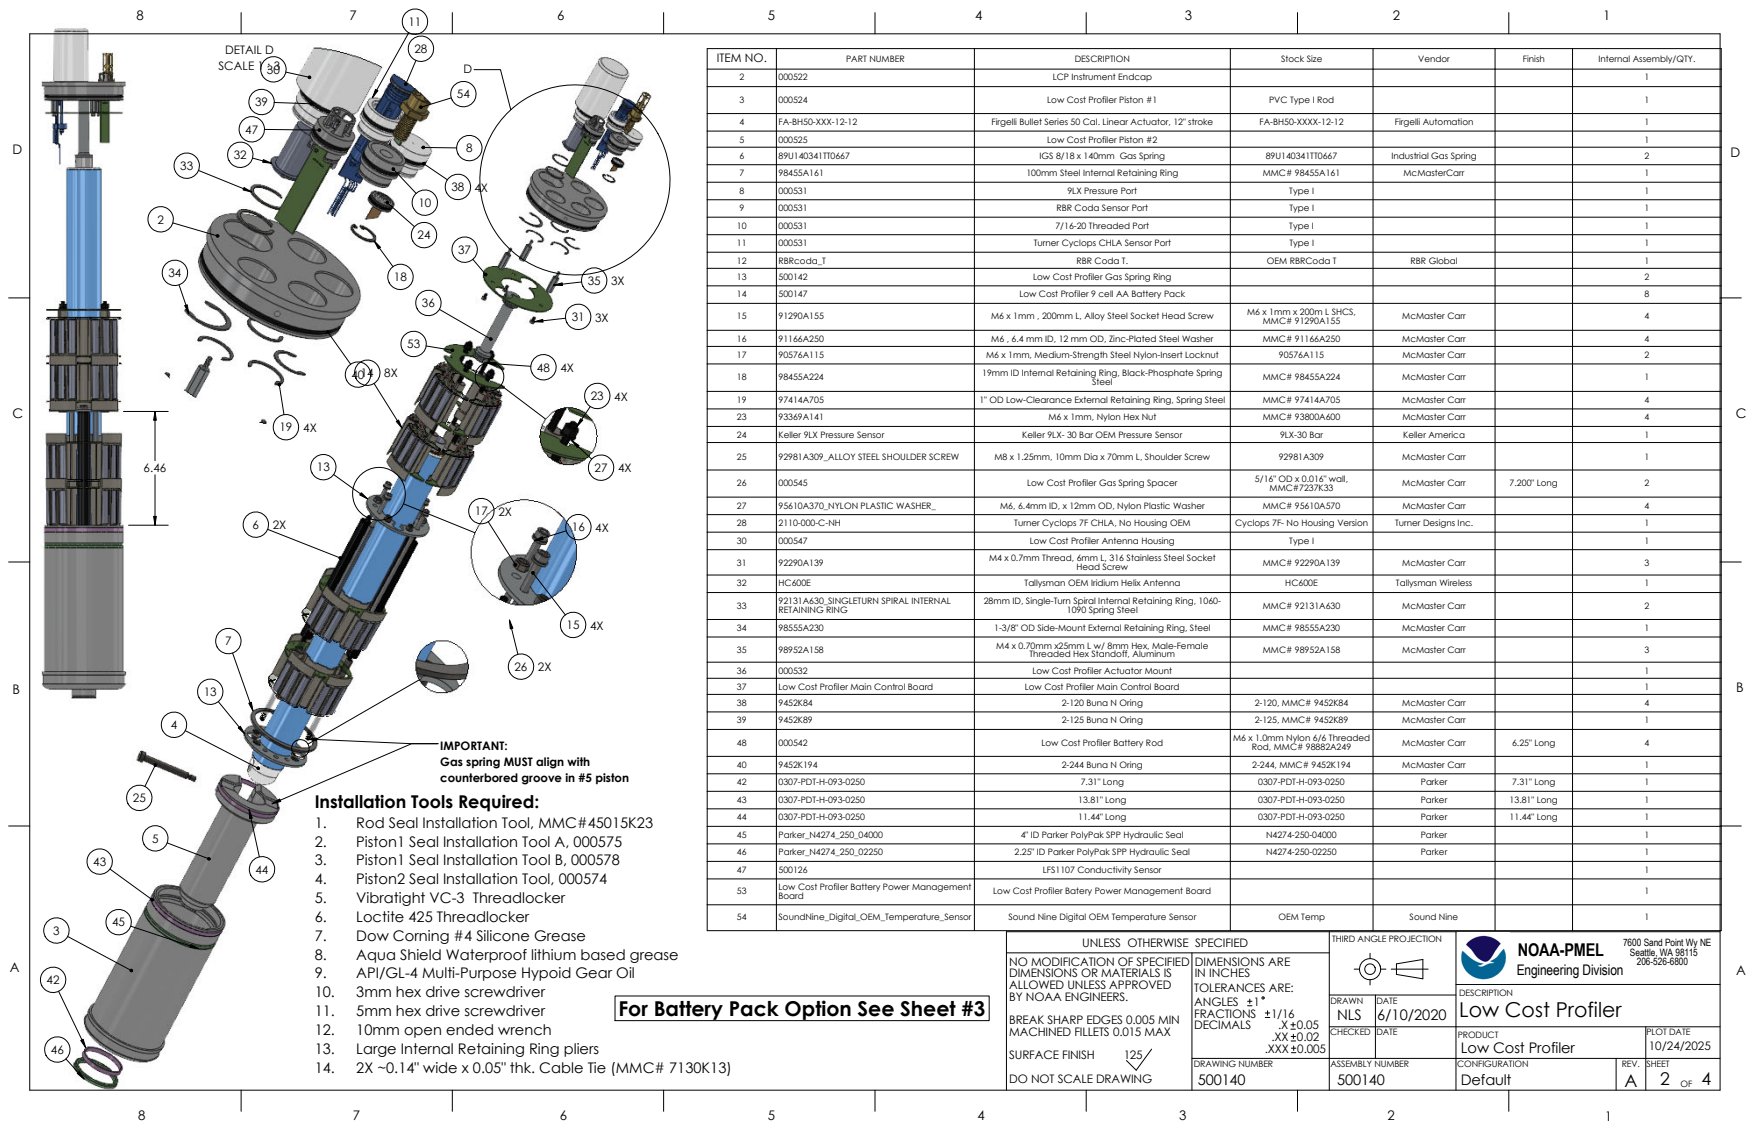
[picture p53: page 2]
DESCRIPTION; DECIMALS; PLOT DATE; DETAIL D SCALE 1 : 3

ITEM NO. | PART NUMBER | DESCRIPTION | Stock Size | Vendor | Finish | Internal Assembly/QTY.

2 | 000522 | LCP Instrument Endcap | | | | 1

3 | 000524 | Low Cost Profiler Piston #1 | PVC Type I Rod | | | 1

4 | FA-BH50-XXX-12-12 | Firgelli Bullet Series 50 Cal. Linear Actuator, 12" stroke | FA-BH50-XXXX-12-12 | Firgelli Automation | | 1
5 | 000525 | Low Cost Profiler Piston #2 | | | | 1
6 | 89U140341TT0667 | IGS 8/18 x 140mm Gas Spring | 89U140341TT0667 | Industrial Gas Spring | | 2
7 | 98455A161 | 100mm Steel Internal Retaining Ring | MMC# 98455A161 | McMasterCarr | | 1
8 | 000531 | 9LX Pressure Port | Type I | | | 1
9 | 000531 | RBR Coda Sensor Port | Type I | | | 1
10 | 000531 | 7/16-20 Threaded Port | Type I | | | 1
11 | 000531 | Turner Cyclops CHLA Sensor Port | Type I | | | 1
12 | RBRcoda_T | RBR Coda T. | OEM RBRCoda T | RBR Global | | 1
13 | 500142 | Low Cost Profiler Gas Spring Ring | | | | 2
14 | 500147 | Low Cost Profiler 9 cell AA Battery Pack | | | | 8
15 | 91290A155 | M6 x 1mm , 200mm L, Alloy Steel Socket Head Screw | M6 x 1mm x 200m L SHCS, MMC# 91290A155 | McMaster Carr | | 4

16 | 91166A250 | M6 , 6.4 mm ID, 12 mm OD, Zinc-Plated Steel Washer | MMC# 91166A250 | McMaster Carr | | 4
17 | 90576A115 | M6 x 1mm, Medium-Strength Steel Nylon-Insert Locknut | 90576A115 | McMaster Carr | | 2
18 | 98455A224 | 19mm ID Internal Retaining Ring, Black-Phosphate Spring Steel | MMC# 98455A224 | McMaster Carr | | 1

19 | 97414A705 | 1" OD Low-Clearance External Retaining Ring, Spring Steel | MMC# 97414A705 | McMaster Carr | | 4
23 | 93369A141 | M6 x 1mm, Nylon Hex Nut | MMC# 93800A600 | McMaster Carr | | 4
24 | Keller 9LX Pressure Sensor | Keller 9LX- 30 Bar OEM Pressure Sensor | 9LX-30 Bar | Keller America | | 1

25 | 92981A309_ALLOY STEEL SHOULDER SCREW | M8 x 1.25mm, 10mm Dia x 70mm L, Shoulder Screw | 92981A309 | McMaster Carr | | 1

26 | 000545 | Low Cost Profiler Gas Spring Spacer | 5/16" OD x 0.016" wall, MMC#7237K33 | McMaster Carr | 7.200" Long | 2

27 | 95610A370_NYLON PLASTIC WASHER_ | M6, 6.4mm ID, x 12mm OD, Nylon Plastic Washer | MMC# 95610A570 | McMaster Carr | | 4
28 | 2110-000-C-NH | Turner Cyclops 7F CHLA, No Housing OEM | Cyclops 7F- No Housing Version | Turner Designs Inc. | | 1
30 | 000547 | Low Cost Profiler Antenna Housing | Type I | | | 1
31 | 92290A139 | M4 x 0.7mm Thread, 6mm L, 316 Stainless Steel Socket Head Screw | MMC# 92290A139 | McMaster Carr | | 3

32 | HC600E | Tallysman OEM Iridium Helix Antenna | HC600E | Tallysman Wireless | | 1
33 | 92131A630_SINGLETURN SPIRAL INTERNAL RETAINING RING | 28mm ID, Single-Turn Spiral Internal Retaining Ring, 1060- 1090 Spring Steel | MMC# 92131A630 | McMaster Carr | | 2

34 | 98555A230 | 1-3/8" OD Side-Mount External Retaining Ring, Steel | MMC# 98555A230 | McMaster Carr | | 1
35 | 98952A158 | M4 x 0.70mm x25mm L w/ 8mm Hex, Male-Female Threaded Hex Standoff, Aluminum | MMC# 98952A158 | McMaster Carr | | 3

36 | 000532 | Low Cost Profiler Actuator Mount | | | | 1
37 | Low Cost Profiler Main Control Board | Low Cost Profiler Main Control Board | | | | 1
38 | 9452K84 | 2-120 Buna N Oring | 2-120, MMC# 9452K84 | McMaster Carr | | 4
39 | 9452K89 | 2-125 Buna N Oring | 2-125, MMC# 9452K89 | McMaster Carr | | 1
48 | 000542 | Low Cost Profiler Battery Rod | M6 x 1.0mm Nylon 6/6 Threaded Rod, MMC# 98882A249 | McMaster Carr | 6.25" Long | 4

IMPORTANT:
Gas spring MUST align with
counterbored groove in #5 piston

40 | 9452K194 | 2-244 Buna N Oring | 2-244, MMC# 9452K194 | McMaster Carr | | 1
42 | 0307-PDT-H-093-0250 | 7.31" Long | 0307-PDT-H-093-0250 | Parker | 7.31" Long | 1
43 | 0307-PDT-H-093-0250 | 13.81" Long | 0307-PDT-H-093-0250 | Parker | 13.81" Long | 1
44 45 | 0307-PDT-H-093-0250 Parker_N4274_250_04000 | 11.44" Long 4" ID Parker PolyPak SPP Hydraulic Seal | 0307-PDT-H-093-0250 N4274-250-04000 | Parker | 11.44" Long | 1 1

Installation Tools Required:
1. Rod Seal Installation Tool, MMC#45015K23
2. Piston1 Seal Installation Tool A, 000575
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

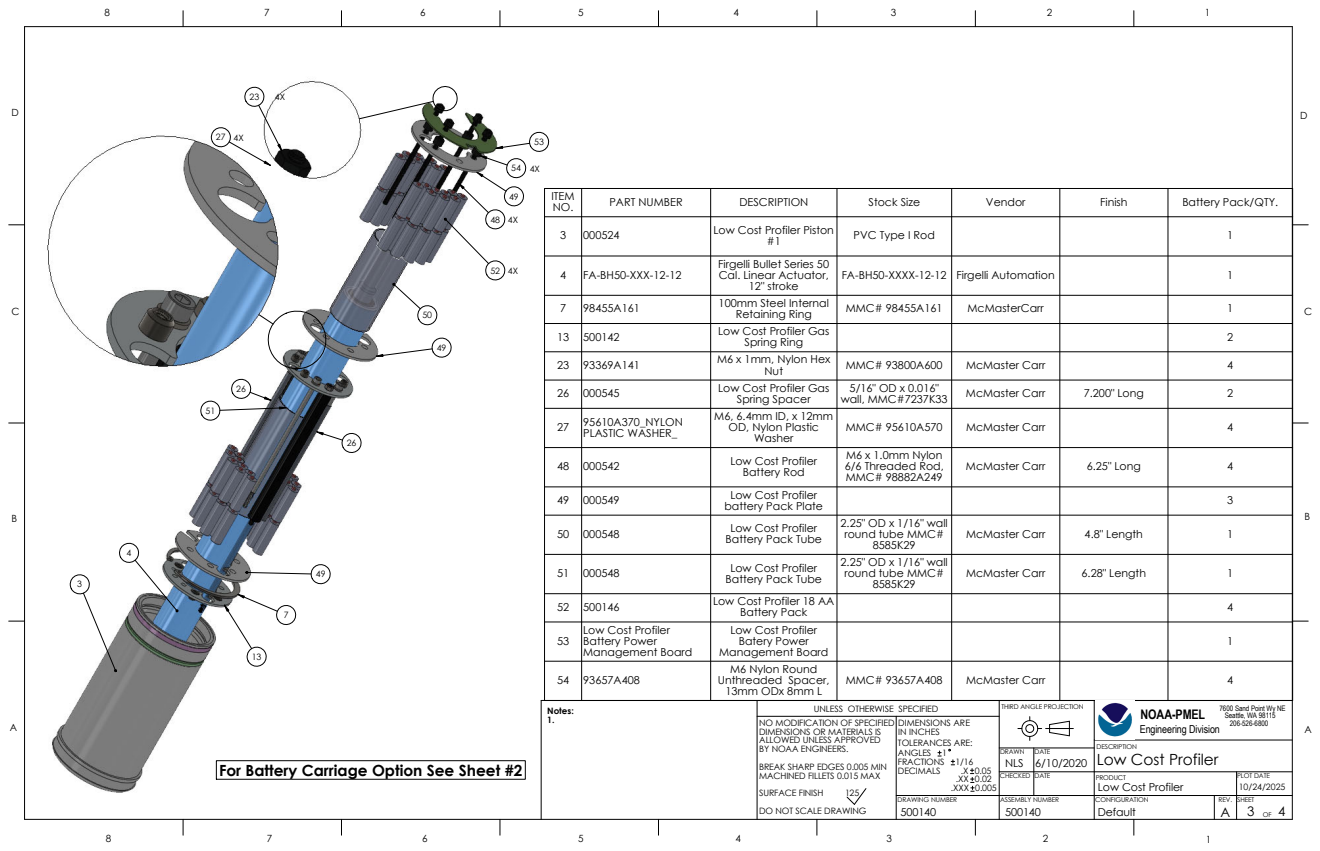
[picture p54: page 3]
DECIMALS; PLOT DATE

ITEM NO. | PART NUMBER | DESCRIPTION | Stock Size | Vendor | Finish | Battery Pack/QTY.

3 | 000524 | Low Cost Profiler Piston #1 | PVC Type I Rod | | | 1

4 | FA-BH50-XXX-12-12 | Firgelli Bullet Series 50 Cal. Linear Actuator, 12" stroke | FA-BH50-XXXX-12-12 | Firgelli Automation | | 1

7 | 98455A161 | 100mm Steel Internal Retaining Ring | MMC# 98455A161 | McMasterCarr | | 1

13 | 500142 | Low Cost Profiler Gas Spring Ring | | | | 2

23 | 93369A141 | M6 x 1mm, Nylon Hex Nut | MMC# 93800A600 | McMaster Carr | | 4

26 | 000545 | Low Cost Profiler Gas Spring Spacer | 5/16" OD x 0.016" wall, MMC#7237K33 | McMaster Carr | 7.200" Long | 2

27 | 95610A370_NYLON PLASTIC WASHER_ | M6, 6.4mm ID, x 12mm OD, Nylon Plastic Washer | MMC# 95610A570 | McMaster Carr | | 4

48 | 000542 | Low Cost Profiler Battery Rod | M6 x 1.0mm Nylon 6/6 Threaded Rod, MMC# 98882A249 | McMaster Carr | 6.25" Long | 4

49 | 000549 | Low Cost Profiler battery Pack Plate | | | | 3

50 | 000548 | Low Cost Profiler Battery Pack Tube | 2.25" OD x 1/16" wall round tube MMC# 8585K29 | McMaster Carr | 4.8" Length | 1

51 | 000548 | Low Cost Profiler Battery Pack Tube | 2.25" OD x 1/16" wall round tube MMC# 8585K29 | McMaster Carr | 6.28" Length | 1

52 | 500146 | Low Cost Profiler 18 AA Battery Pack | | | | 4

53 | Low Cost Profiler Battery Power Management Board | Low Cost Profiler Batery Power Management Board | | | | 1

54 | 93657A408 | M6 Nylon Round Unthreaded Spacer, 13mm ODx 8mm L | MMC# 93657A408 | McMaster Carr | | 4

Notes: 1. | UNLESS OTHERWISE SPECIFIED | THIRD ANGLE PROJECTION | 7600 Sand Point Wy NE NOAA-PMEL Seattle, WA 98115 206-526-6800 Engineering Division

NO MODIFICATION OF SPECIFIED DIMENSIONS OR MATERIALS IS ALLOWED UNLESS APPROVED BY NOAA ENGINEERS. BREAK SHARP EDGES 0.005 MIN MACHINED FILLETS 0.015 MAX | DIMENSIONS ARE IN INCHES TOLERANCES ARE: ANGLES 1 FRACTIONS 1/16 .X 0.05 .XX 0.02

DRAWN NLS | DATE 6/10/2020

DESCRIPTION
Low Cost Profiler

For Battery Carriage Option See Sheet #2

CHECKED | DATE | PRODUCT Low Cost Profiler

D

B

A

B

C

D

A

UNLESS OTHERWISE SPECIFIED | THIRD ANGLE PROJECTION | 7600 Sand Point Wy NE NOAA-PMEL Seattle, WA 98115 206-526-6800 Engineering Division
NO MODIFICATION OF SPECIFIED DIMENSIONS OR MATERIALS IS ALLOWED UNLESS APPROVED BY NOAA ENGINEERS. BREAK SHARP EDGES 0.005 MIN MACHINED FILLETS 0.015 MAX | DIMENSIONS ARE IN INCHES TOLERANCES ARE: ANGLES 1 FRACTIONS 1/16 .X 0.05 .XX 0.02

DESCRIPTION
Low Cost Profiler
DRAWN NLS | DATE 6/10/2020
CHECKED | DATE | PRODUCT Low Cost Profiler
DECIMALS | PLOT DATE

C

Inner Assembly Installation Instructions:
1. Unscrew the Actuator #4's rod end fitting from the rod, being careful to not unscrew the rod from the actuator. After rod end is removed, double check that the rod still fully screwed into the actuator.
2. Lightly Coat # 36 with vibratight threadlocker, wait 15+min & screw into #4. Double check that #4's rod is fully screwed into the actuator.
3. Lightly grease with Aqua Shield & install #46 into #3 using Rod Seal Installation Tool: MMC#45015K23
4. Lightly grease with Aqua Shield & install #45 onto #3 using Piston1 Seal Installation Tool A Assembly, 500195, & Tool B, 000578.
5. Clean #25 threads with IPA and coat with Vibratight threadlocker, wait 15+ min & attach #4 to #5 with #25.
6. Install #42 into #3.
7. <PARA >Generously grease interior bore of #3 and OD of #5 with Aqua Shield grease.
8. Install Piston2 Seal Installation Tool, 000574, onto #5.
9. Install #44 onto #5 so that the ends of #44 join in the middle of #5's wire clearance cutout.
10. Insert #5 into #3, you can use a pair of needle nose pliers to gently pull on the end of #44 during installation. After installation, move actuator cable to the inside of the wear ring.
11. Remove Piston2 Seal Installation Tool, 000574.
12. Pass the #4 actuator's cable thru lower #13, using of of the gas spring mounting holes which are 90 from the ear cutouts.
13. Make sure piston #5 is fully extended in #3, Fully seat #13 in #3, pull the cable tight and mark where it exits the top of #13. Remove #13, then measure 1" from mark on cable towards the cable's bitter end and install a ziptie around the cable (MMC#7130K13), tight enough that it does not move on the cable.
14. Retract piston #5 and install lower #13 as shown into #3. Mark location of #13 gas spring ear cutouts on #3's ID so that they align with the 2 counterbored slots in the top of #5. Then fully extend piston #5. Secure #13 to #3 with #7, making sure to install #7 so that its free ends are 180 from the actuator cable.
15. Add a second ziptie (MMC#7130K13) around the cable ~ 0.25" above where cable exits #13 plate.
16. 2X: Bolt #6 to Upper #13 as shown with #17.
17. 4x: Coat #15 threads with Vibratight threadlocker, wait 15+ min, install #16 & pass thru upper #13.
18. 2X: Pass #15 thru #26, place on opposite sides from each other.
19. Lower Battery Installation: IMPORTANT: Make sure that #6 gas spring free ends are aligned with the 2 counterbored slots in #5.
1. Battery Carriage: Slide lower 4 battery packs #14 over #13-15-16-26 assembly & bolt (hand tight) to #3-13-7-4-5 assembly.
2. Battery Pack: Slide #49 & #51 over the #3-13-7-4 assembly. Then install 2X lower battery packs #52, 500146, use foam to sandwich battery packs & bolt #13-15-16-26 assembly to #3-13-7-4 assembly. Route actuator cable thru slot in #49.
20. Tighten bolts, slowly working your way between opposing bolt side (like tightening a flange) until #26s are hard sandwiched between upper and lower #13s. Double check that the dimension between the bottom of the upper #13 and the top face of #3 is 6.42" (as shown at both gas spring mounting locations). Adjust to meet the 6.42" dimension if needed.
21. Upper Battery Installation:
1. Battery Carriage: 4X: Bolt upper battery packs #14 & power management board #53 to upper #13 plate with #48 & #23& #27, use Loctite 425 threadlocker on all connections. Route actuator cable along slots in the OD of lower #14, thru the ear cutout in upper #13, and along slots in upper #14.
2. Battery Pack: Slide second #49 & #50 over #4. Then install 2X upper battery packs #52, 500146, use foam to sandwich battery packs. Slide third #49 over #4. Install 4X #54 & Battery management board #53. Bolt #49-50-52-53-53 assembly to upper #13 plate with 4X: #48 & #23& #27, use Loctite 425 threadlocker on all connections. Route actuator cable along gas spring, thru the ear cutout in upper #13 and 2X upper #49s.
22. Remove any slack from, and securely tape, the actuator's cable tight around the blue actuator housing ~1" down from where the rod exits the blue housing.
Sensor Endcap Installation Instructions:
1. Insert #32 into #30 and secure with #33.
2. 3X: Assemble sensors into 000531 sensor ports.
3. Place tape over top of 000531 pressure port hole, #8, place face down and fill sensor cup with API/GL-4 Multi-Purpose Hypoid Gear oil. Gently install #24 into #8 using the oil as a lubricant, secure in place with #18. Remove tape.
4. Install #40 onto #2, #39 onto #30, and 4X #38 onto 00531, lightly grease O-rings and the IDs of the #2 ports with Dow Corning #4 silicone grease. Install into #2 as shown and secure with 4X #19 & #34.
5. Attach #37 to #2 with 3X: #35 & #31, use Loctite 425 on all connections.

For Battery Pack Option See Sheet #3

For Battery Carriage Option See Sheet #2

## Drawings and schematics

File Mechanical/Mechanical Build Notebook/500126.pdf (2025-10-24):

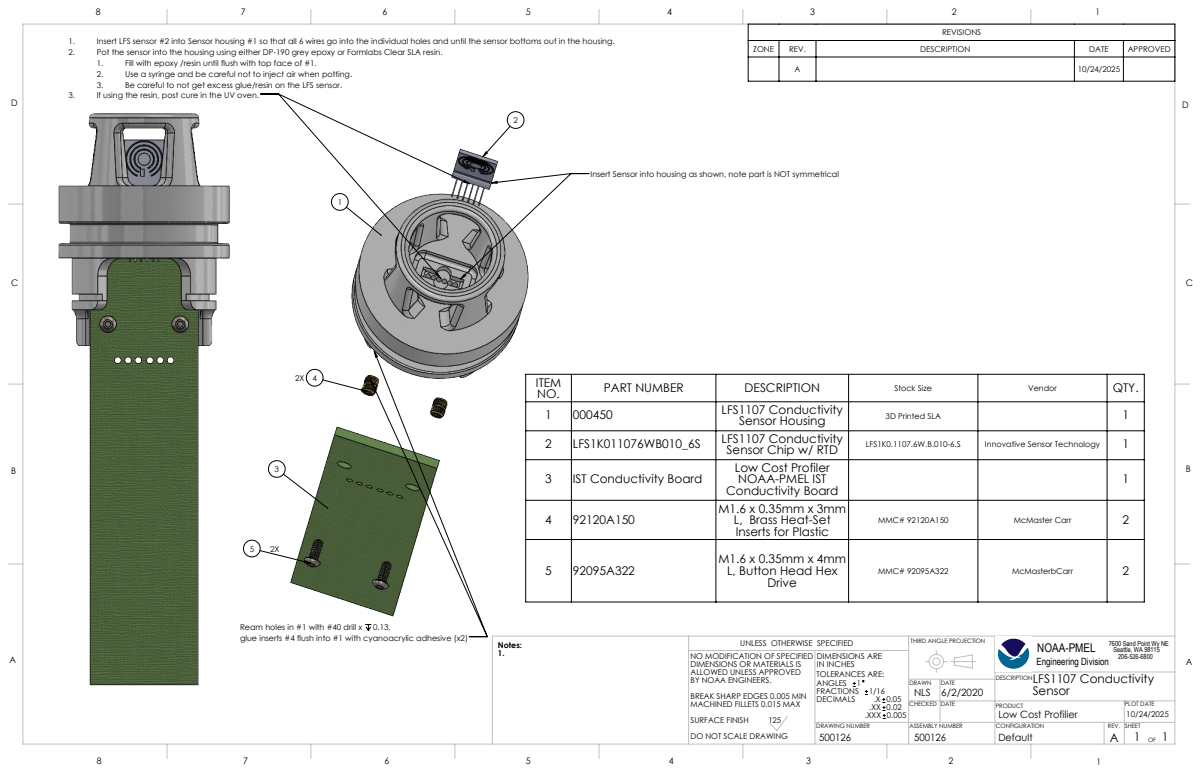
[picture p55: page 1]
.X 0.05 .XX 0.02 .XXX 0.005; DRAWING NUMBER; TOLERANCES ARE:; DATE; SURFACE FINISH; ANGLES 1 FRACTIONS 1/16; DECIMALS; PLOT DATE; DIMENSIONS ARE IN INCHES; ASSEMBLY NUMBER

1. Insert LFS sensor #2 into Sensor housing #1 so that all 6 wires go into the individual holes and until the sensor bottoms out in the housing.
2. Pot the sensor into the housing using either DP-190 grey epoxy or Formlabs Clear SLA resin.
1. Fill with epoxy /resin until flush with top face of #1.
2. Use a syringe and be careful not to inject air when potting.
3. Be careful to not get excess glue/resin on the LFS sensor.
3. If using the resin, post cure in the UV oven.

ZONE | REV. | DESCRIPTION | DATE | APPROVED

Insert Sensor into housing as shown, note part is NOT symmetrical

ITEM NO. | PART NUMBER | DESCRIPTION | Stock Size | Vendor | QTY.
1 | 000450 | LFS1107 Conductivity Sensor Housing | 3D Printed SLA | | 1
2 | LFS1K011076WB010_6S | LFS1107 Conductivity Sensor Chip w/ RTD | LFS1K0.1107.6W.B.010-6.S | Innovative Sensor Technology | 1
3 | IST Conductivity Board | Low Cost Profiler NOAA-PMEL IST Conductivity Board | | | 1

4 | 92120A150 | M1.6 x 0.35mm x 3mm L, Brass Heat-Set Inserts for Plastic | MMC# 92120A150 | McMaster Carr | 2

5 | 92095A322 | M1.6 x 0.35mm x 4mm L, Button Head Hex Drive | MMC# 92095A322 | McMasterbCarr | 2

Ream holes in #1 with #40 drill x 0.13,
glue inserts #4 flush into #1 with cyanoacrylic adhesive (x2)

UNLESS OTHERWISE SPECIFIED

THIRD ANGLE PROJECTION

NOAA-PMEL
Engineering Division
LFS1107 Conductivity
Sensor
Low Cost Profilier

7600 Sand Point Wy NE
Seattle, WA 98115

NO MODIFICATION OF SPECIFIED
DIMENSIONS OR MATERIALS IS
ALLOWED UNLESS APPROVED
BY NOAA ENGINEERS.
BREAK SHARP EDGES 0.005 MIN
MACHINED FILLETS 0.015 MAX
DO NOT SCALE DRAWING

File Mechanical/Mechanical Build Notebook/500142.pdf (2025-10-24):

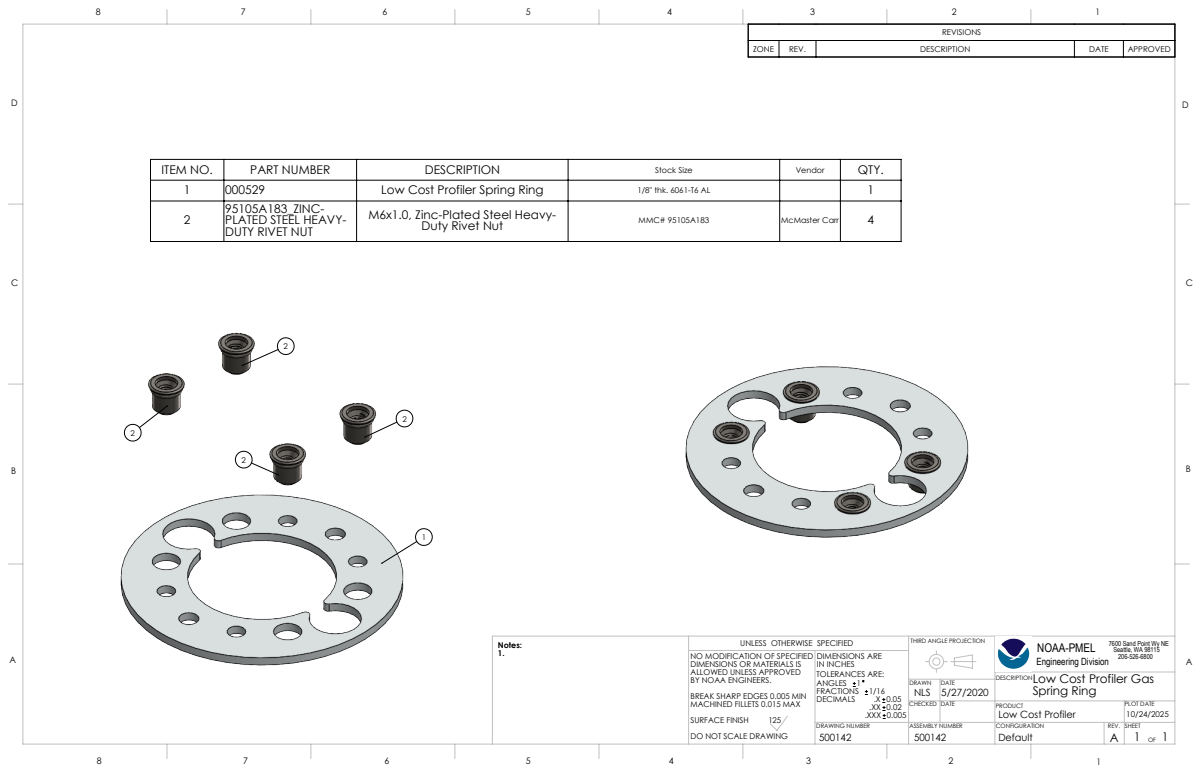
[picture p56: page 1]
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

ITEM NO. | PART NUMBER | DESCRIPTION | Stock Size | Vendor | QTY.
1 | 000529 | Low Cost Profiler Spring Ring | 1/8" thk. 6061-T6 AL | | 1
2 | 95105A183_ZINC-PLATED STEEL HEAVY-DUTY RIVET NUT | M6x1.0, Zinc-Plated Steel Heavy-Duty Rivet Nut | MMC# 95105A183 | McMaster Carr | 4

UNLESS OTHERWISE SPECIFIED

THIRD ANGLE PROJECTION

NOAA-PMEL
Engineering Division
Low Cost Profiler Gas
Spring Ring
Low Cost Profiler

7600 Sand Point Wy NE
Seattle, WA 98115

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

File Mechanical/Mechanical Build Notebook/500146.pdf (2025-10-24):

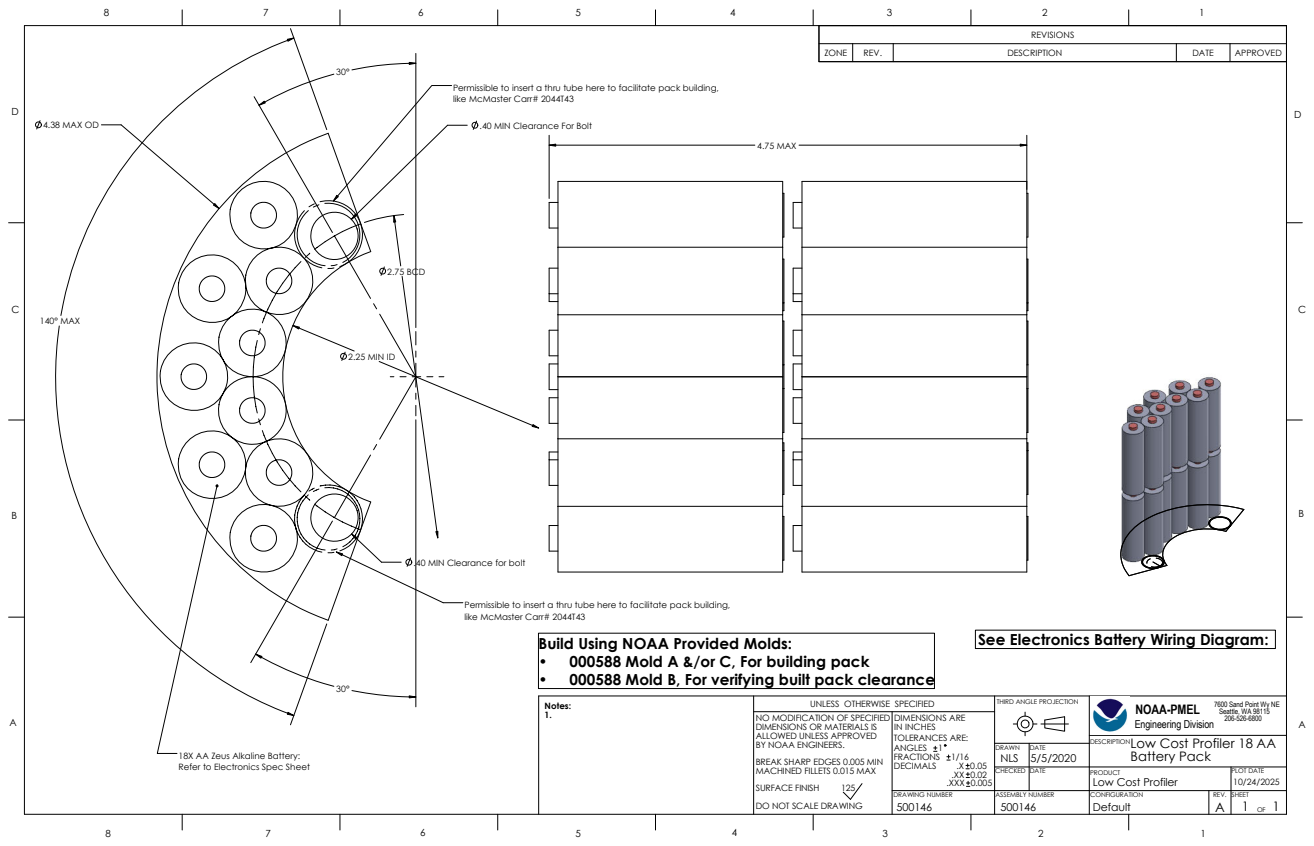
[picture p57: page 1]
2.25 MIN ID; 4.38 MAX OD; 140° MAX; 2.75 BCD; DESCRIPTION; PLOT DATE; NO MODIFICATION OF SPECIFIED; SHEET; Seattle, WA 98115; Notes:; 7600 Sand Point Wy NE; REVISIONS; ZONE; REV.; DATE; APPROVED; Build Using NOAA Provided Molds:; See Electronics Battery Wiring Diagram:; 4.75 MAX

Permissible to insert a thru tube here to facilitate pack building,
like McMaster Carr# 2044T43

.40 MIN Clearance For Bolt

.40 MIN Clearance for bolt

• 000588 Mold A &/or C, For building pack
• 000588 Mold B, For verifying built pack clearance

1. | UNLESS OTHERWISE SPECIFIED | THIRD ANGLE PROJECTION

NOAA-PMEL
Engineering Division
Low Cost Profiler 18 AA
Battery Pack

DIMENSIONS OR MATERIALS IS ALLOWED UNLESS APPROVED BY NOAA ENGINEERS. MACHINED FILLETS 0.015 MAX SURFACE FINISH 125 DO NOT SCALE DRAWING | DIMENSIONS ARE IN INCHES TOLERANCES ARE: ANGLES 1 FRACTIONS 1/16 DECIMALS BREAK SHARP EDGES 0.005 MIN .X 0.05 .XX 0.02 .XXX 0.005

DRAWN NLS | DATE 5/5/2020

18X AA Zeus Alkaline Battery:
Refer to Electronics Spec Sheet

CHECKED | DATE | PRODUCT Low Cost Profiler

DRAWING NUMBER 500146 | ASSEMBLY NUMBER 500146 | CONFIGURATION Default | REV. A

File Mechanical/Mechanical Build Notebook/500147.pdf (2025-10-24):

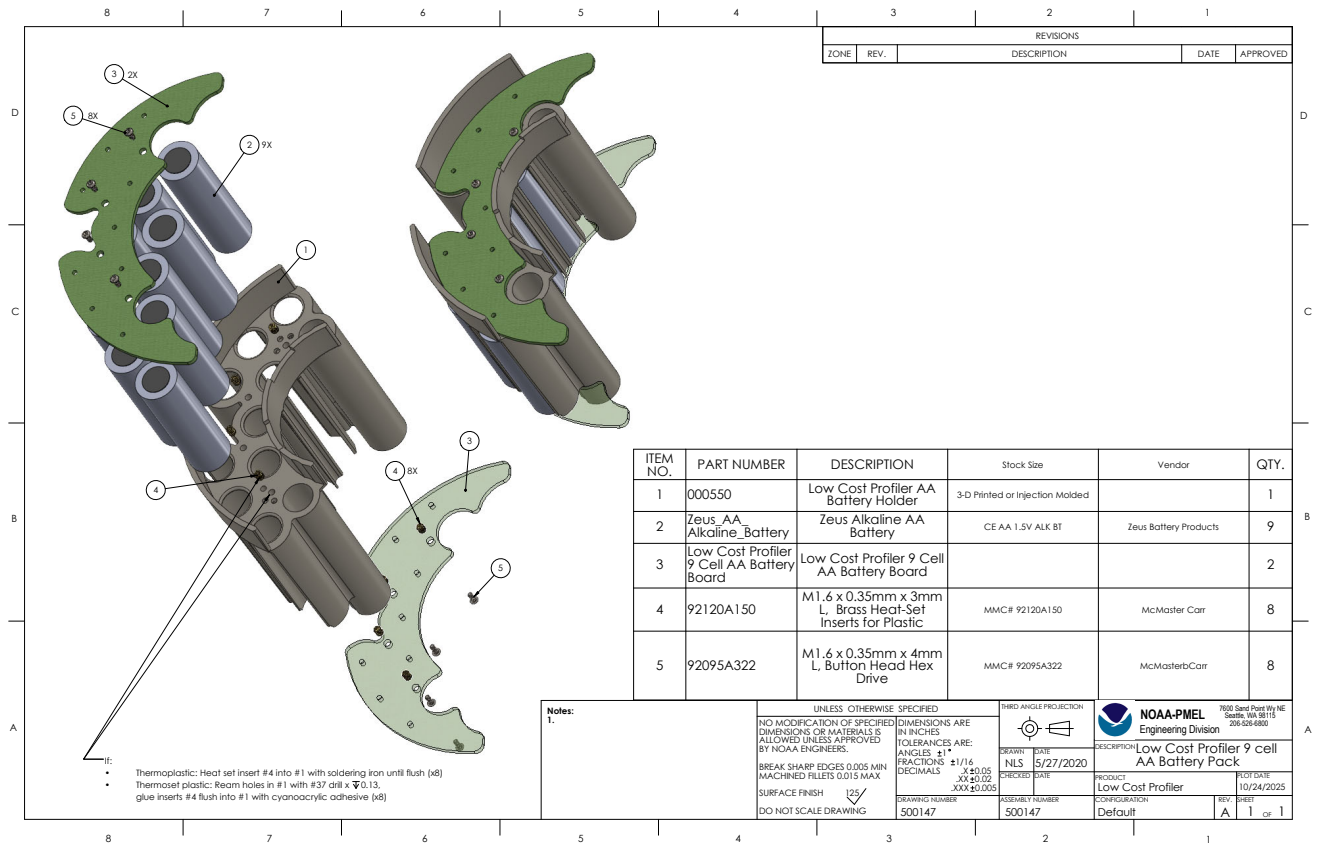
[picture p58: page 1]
DESCRIPTION; PLOT DATE; NO MODIFICATION OF SPECIFIED; SHEET; Seattle, WA 98115; Notes:; 7600 Sand Point Wy NE; Thermoset plastic: Ream holes in #1 with #37 drill x; REVISIONS; ZONE; REV.; DATE; APPROVED

ITEM NO. | PART NUMBER | DESCRIPTION | Stock Size | Vendor | QTY.
1 | 000550 | Low Cost Profiler AA Battery Holder | 3-D Printed or Injection Molded | | 1

2 | Zeus_AA_ Alkaline_Battery | Zeus Alkaline AA Battery | CE AA 1.5V ALK BT | Zeus Battery Products | 9

3 | Low Cost Profiler 9 Cell AA Battery Board | Low Cost Profiler 9 Cell AA Battery Board | | | 2

4 | 92120A150 | M1.6 x 0.35mm x 3mm L, Brass Heat-Set Inserts for Plastic | MMC# 92120A150 | McMaster Carr | 8

5 | 92095A322 | M1.6 x 0.35mm x 4mm L, Button Head Hex Drive | MMC# 92095A322 | McMasterbCarr | 8

1. | UNLESS OTHERWISE SPECIFIED | THIRD ANGLE PROJECTION

NOAA-PMEL
Engineering Division
Low Cost Profiler 9 cell
AA Battery Pack

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

DRAWN NLS | DATE 5/27/2020

• Thermoplastic: Heat set insert #4 into #1 with soldering iron until flush (x8)
glue inserts #4 flush into #1 with cyanoacrylic adhesive (x8)

CHECKED | DATE | PRODUCT Low Cost Profiler

DRAWING NUMBER 500147 | ASSEMBLY NUMBER 500147 | CONFIGURATION Default | REV. A

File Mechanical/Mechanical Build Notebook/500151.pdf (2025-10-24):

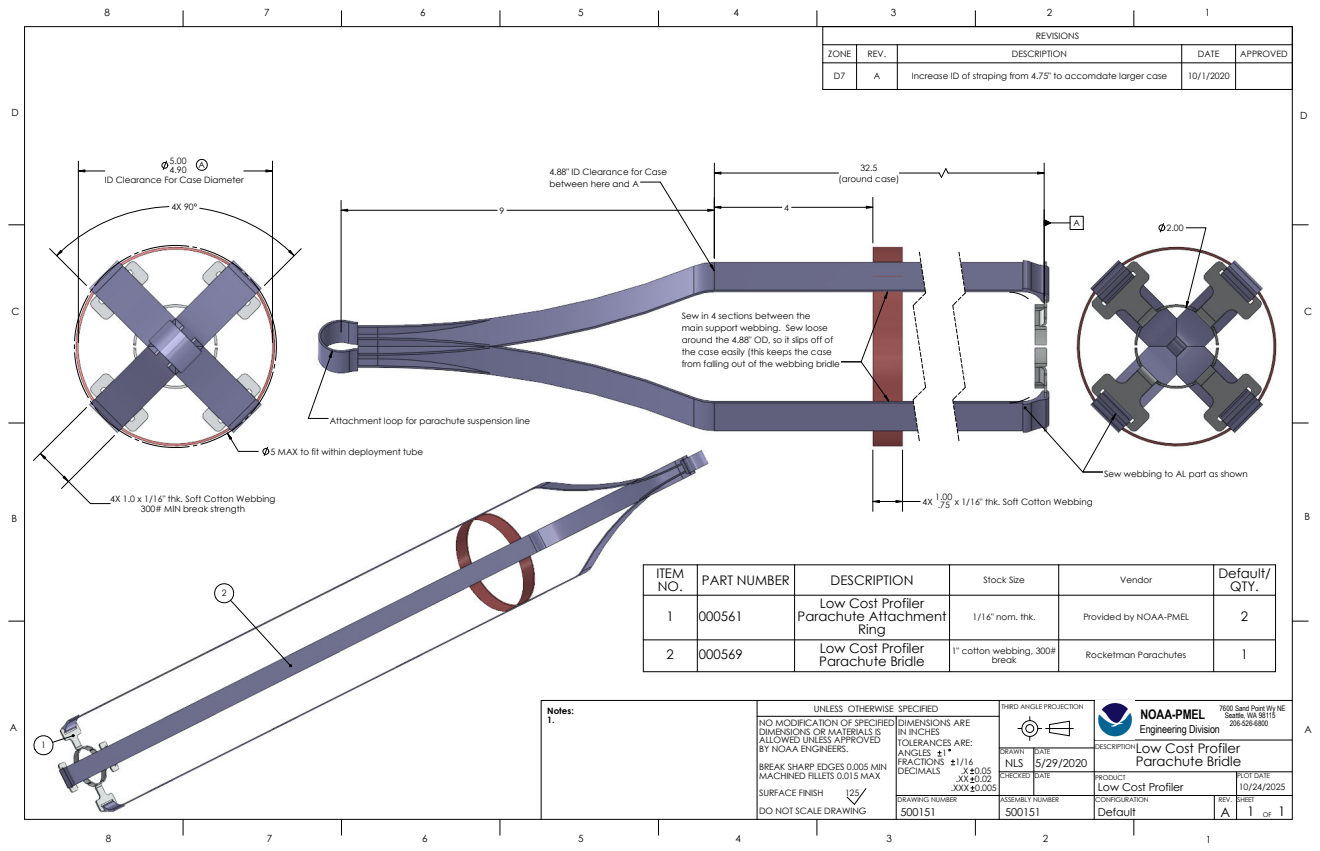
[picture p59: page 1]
DESCRIPTION; PLOT DATE; NO MODIFICATION OF SPECIFIED; SHEET; Seattle, WA 98115; Notes:; 7600 Sand Point Wy NE; REVISIONS; 32.5 (around case)

ZONE | REV. | DESCRIPTION | DATE | APPROVED

D7 | A | Increase ID of straping from 4.75" to accomdate larger case | 10/1/2020

4.88" ID Clearance for Case
between here and A

ID Clearance For Case Diameter

Sew in 4 sections between the
main support webbing. Sew loose
around the 4.88" OD, so it slips off of
the case easily (this keeps the case
from falling out of the webbing bridle

Attachment loop for parachute suspension line

5 MAX to fit within deployment tube

Sew webbing to AL part as shown

4X 1.0 x 1/16" thk. Soft Cotton Webbing
300# MIN break strength

4X 1.00 .75 x 1/16" thk. Soft Cotton Webbing

ITEM NO. | PART NUMBER | DESCRIPTION | Stock Size | Vendor | Default/ QTY.
1 | 000561 | Low Cost Profiler Parachute Attachment Ring | 1/16" nom. thk. | Provided by NOAA-PMEL | 2

2 | 000569 | Low Cost Profiler Parachute Bridle | 1" cotton webbing, 300# break | Rocketman Parachutes | 1

1. | UNLESS OTHERWISE SPECIFIED | THIRD ANGLE PROJECTION

NOAA-PMEL
Engineering Division
Low Cost Profiler
Parachute Bridle

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

DRAWN NLS | DATE 5/29/2020

CHECKED | DATE | PRODUCT Low Cost Profiler

DRAWING NUMBER 500151 | ASSEMBLY NUMBER 500151 | CONFIGURATION Default | REV. A

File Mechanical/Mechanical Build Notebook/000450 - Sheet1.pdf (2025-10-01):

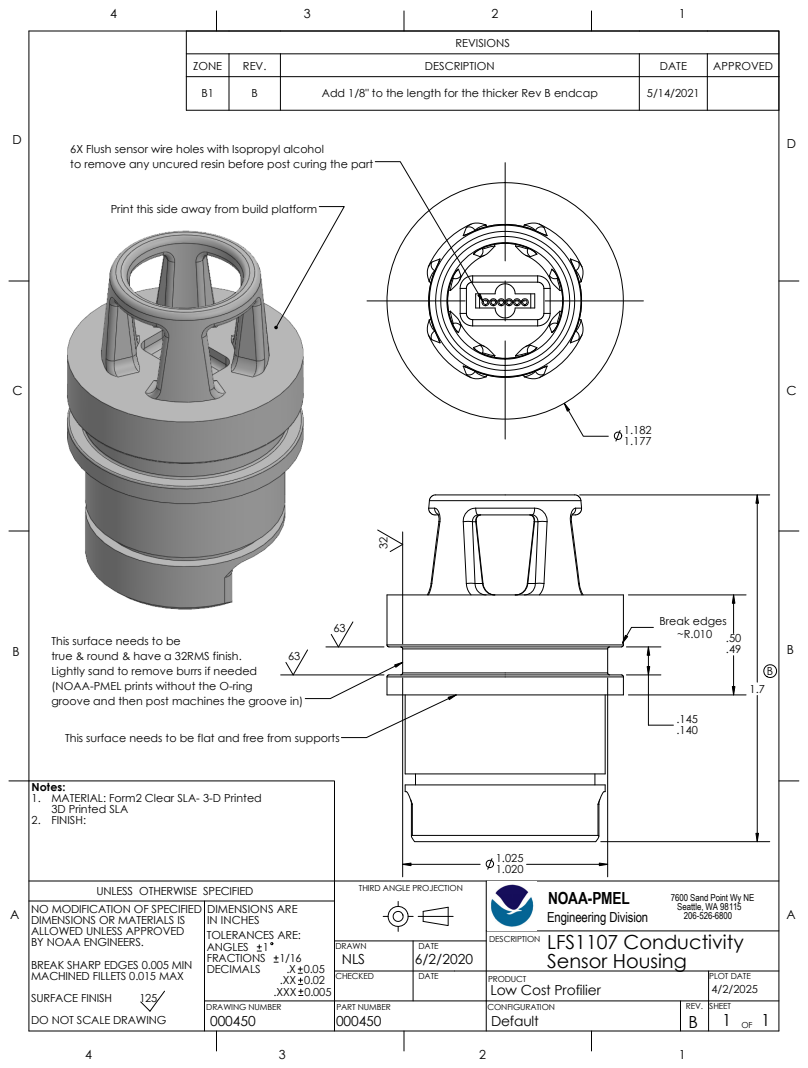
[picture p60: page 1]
NOAA-PMEL; FINISH:; SHEET; 3D Printed SLA; LFS1107 Conductivity; Engineering Division; PLOT DATE; Notes:; Sensor Housing; DESCRIPTION; Break edges ~R.010 .50 .49; REVISIONS

ZONE | REV. | DESCRIPTION | DATE | APPROVED

B1 | B | Add 1/8" to the length for the thicker Rev B endcap | 5/14/2021

6X Flush sensor wire holes with Isopropyl alcohol
to remove any uncured resin before post curing the part

Print this side away from build platform

This surface needs to be
true & round & have a 32RMS finish.
Lightly sand to remove burrs if needed
(NOAA-PMEL prints without the O-ring
groove and then post machines the groove in)

This surface needs to be flat and free from supports

MATERIAL: Form2 Clear SLA- 3-D Printed

UNLESS OTHERWISE SPECIFIED | THIRD ANGLE PROJECTION

7600 Sand Point Wy NE
Seattle, WA 98115

NO MODIFICATION OF SPECIFIED DIMENSIONS OR MATERIALS IS ALLOWED UNLESS APPROVED BY NOAA ENGINEERS. BREAK SHARP EDGES 0.005 MIN MACHINED FILLETS 0.015 MAX SURFACE FINISH 125 DO NOT SCALE DRAWING | DIMENSIONS ARE IN INCHES TOLERANCES ARE: ANGLES 1 FRACTIONS 1/16 DECIMALS .X 0.05 .XX 0.02 .XXX 0.005

DRAWN NLS | DATE 6/2/2020

CHECKED | DATE | PRODUCT Low Cost Profilier

DRAWING NUMBER 000450 | PART NUMBER 000450 | CONFIGURATION Default | REV. B

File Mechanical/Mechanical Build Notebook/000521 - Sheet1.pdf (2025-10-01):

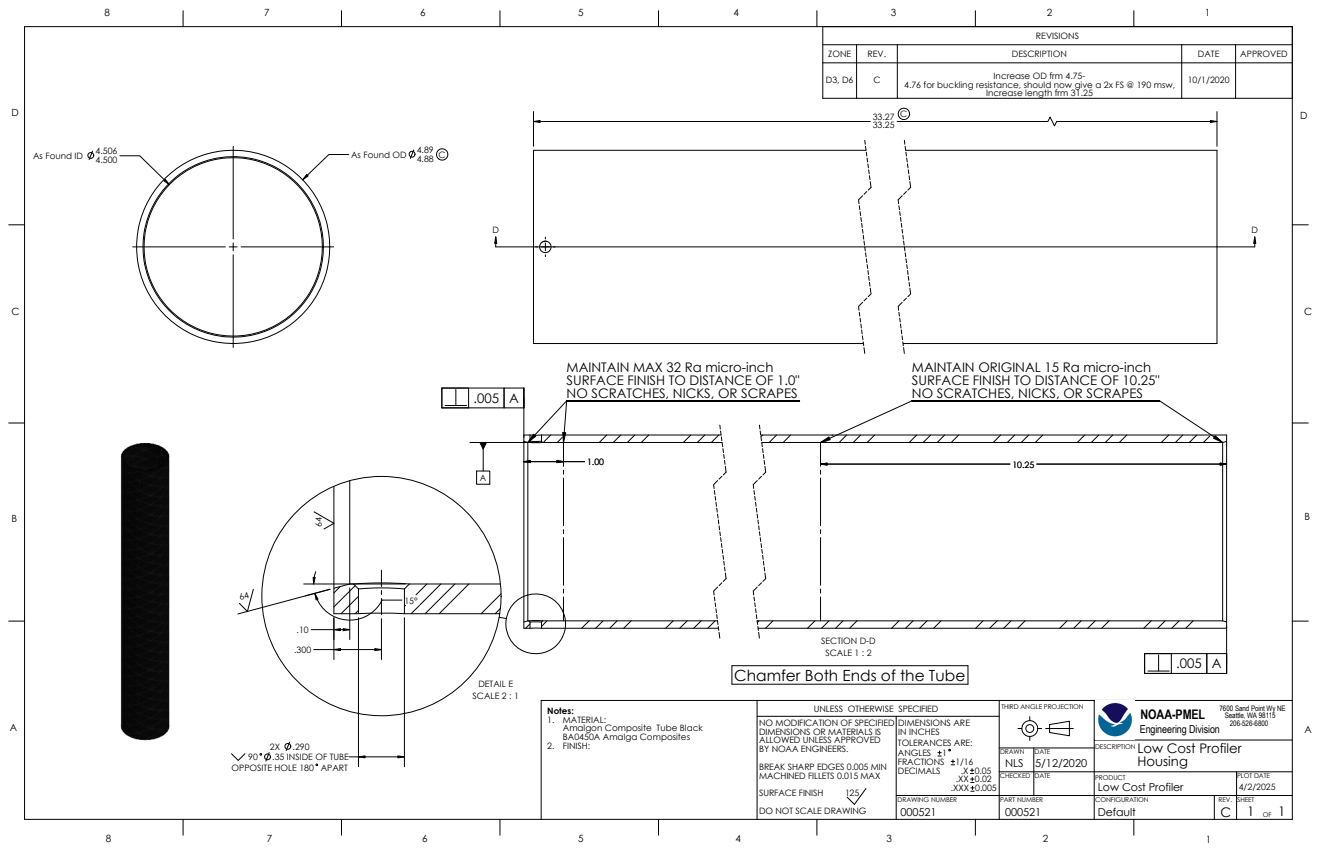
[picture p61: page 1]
REV.; Default; PART NUMBER; .XXX; DIMENSIONS ARE; CHECKED; DRAWN NLS; TOLERANCES ARE:; DESCRIPTION; MACHINED FILLETS 0.015 MAX; PLOT DATE; SURFACE FINISH; IN INCHES; DRAWING NUMBER; DATE; FRACTIONS; NO MODIFICATION OF SPECIFIED; SHEET; BREAK SHARP EDGES 0.005 MIN; DECIMALS; ANGLES; As Found ID 4.506 4.500; As Found OD 4.89 4.88; DETAIL E SCALE 2 : 1; .35 INSIDE OF TUBE; SCALE 1 : 2; SECTION D-D; NO SCRATCHES, NICKS, OR SCRAPES

REVISIONS

ZONE | REV. | DESCRIPTION | DATE | APPROVED

D3, D6 | C | Increase OD frm 4.75- 4.76 for buckling resistance, should now give a 2x FS @ 190 msw, Increase length frm 31.25 | 10/1/2020

MAINTAIN MAX 32 Ra micro-inch
SURFACE FINISH TO DISTANCE OF 1.0"
NO SCRATCHES, NICKS, OR SCRAPES

MAINTAIN ORIGINAL 15 Ra micro-inch
SURFACE FINISH TO DISTANCE OF 10.25"

Chamfer Both Ends of the Tube

UNLESS OTHERWISE SPECIFIED

THIRD ANGLE PROJECTION

7600 Sand Point Wy NE
Seattle, WA 98115

Notes:
1. MATERIAL:
Amalgon Composite Tube Black
BA0450A Amalga Composites
FINISH:

NOAA-PMEL
Engineering Division
Low Cost Profiler
Housing

DIMENSIONS OR MATERIALS IS
ALLOWED UNLESS APPROVED
BY NOAA ENGINEERS.
DO NOT SCALE DRAWING

OPPOSITE HOLE 180 APART

PRODUCT
CONFIGURATION

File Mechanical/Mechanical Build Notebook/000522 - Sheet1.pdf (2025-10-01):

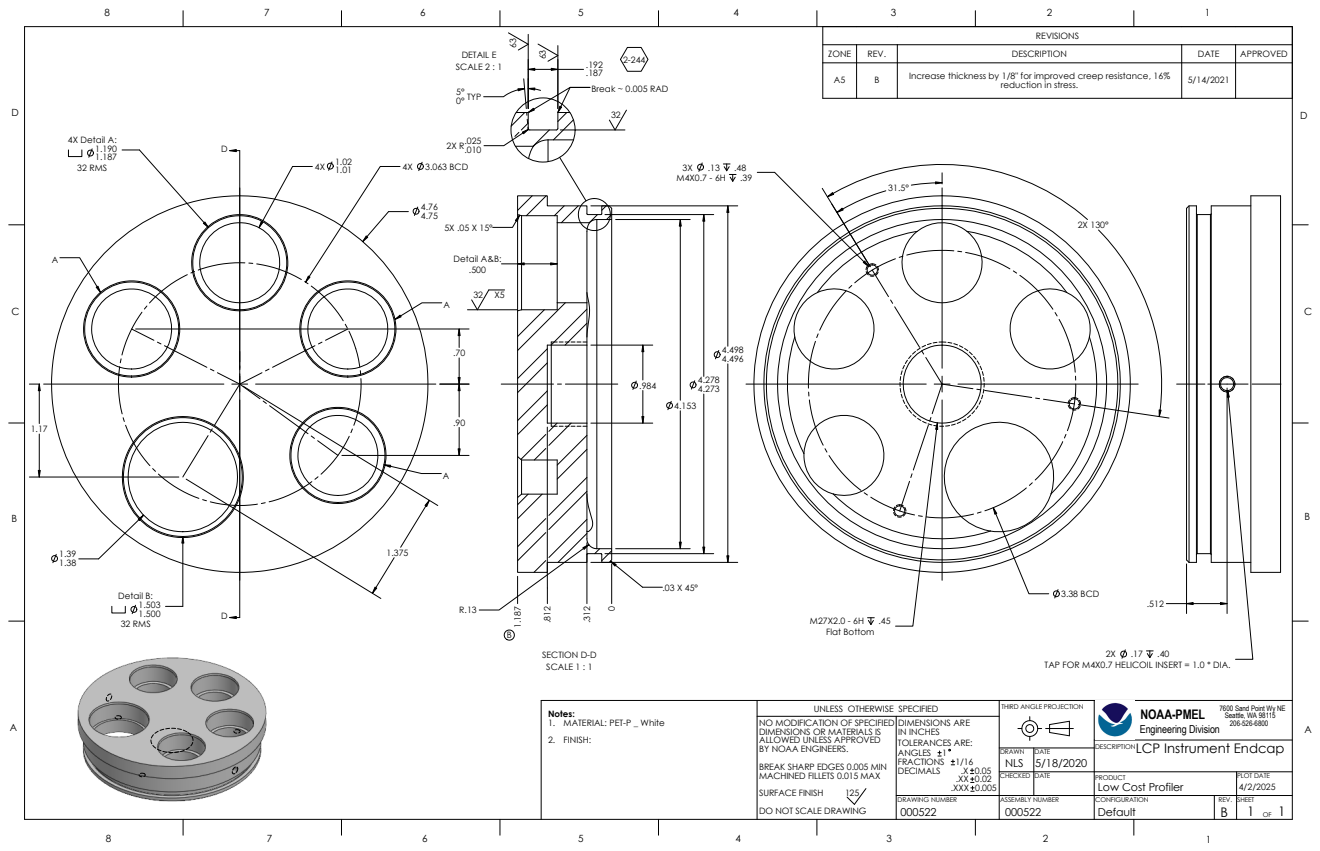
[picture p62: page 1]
5° 0° TYP; 4X 3.063 BCD; 3.38 BCD; DESCRIPTION; MACHINED FILLETS 0.015 MAX; PLOT DATE; NO MODIFICATION OF SPECIFIED; SHEET; SCALE 1 : 1; SECTION D-D; Detail A&B:; SCALE 2 : 1; DETAIL E; Break ~ 0.005 RAD; REVISIONS; 32 RMS; 4X Detail A:; Detail B:; Flat Bottom

ZONE | REV. | DESCRIPTION | DATE | APPROVED

A5 | B | Increase thickness by 1/8" for improved creep resistance, 16% reduction in stress. | 5/14/2021

TAP FOR M4X0.7 HELICOIL INSERT = 1.0 * DIA.

Notes: 1. MATERIAL: PET-P _ White 2. FINISH: | UNLESS OTHERWISE SPECIFIED | THIRD ANGLE PROJECTION

7600 Sand Point Wy NE
Seattle, WA 98115

NOAA-PMEL
Engineering Division
LCP Instrument Endcap

DIMENSIONS OR MATERIALS IS ALLOWED UNLESS APPROVED BY NOAA ENGINEERS. BREAK SHARP EDGES 0.005 MIN SURFACE FINISH 125 DO NOT SCALE DRAWING | DIMENSIONS ARE IN INCHES TOLERANCES ARE: ANGLES 1 FRACTIONS 1/16 DECIMALS .X 0.05 .XX 0.02 .XXX 0.005

DRAWN NLS | DATE 5/18/2020

CHECKED | DATE | PRODUCT Low Cost Profiler

DRAWING NUMBER 000522 | ASSEMBLY NUMBER 000522 | CONFIGURATION Default | REV. B

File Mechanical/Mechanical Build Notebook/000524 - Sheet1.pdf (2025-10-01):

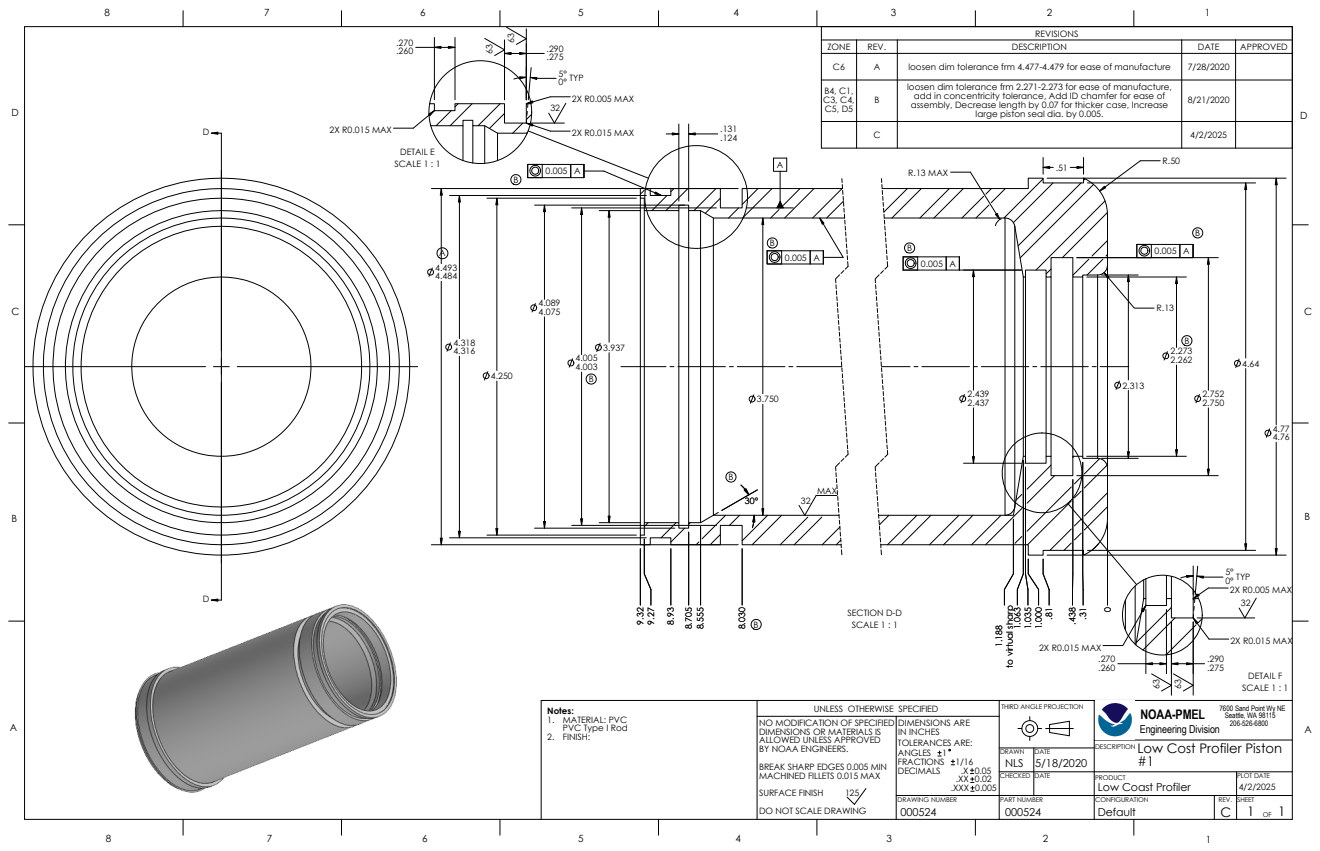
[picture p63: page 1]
5° 0° TYP; REV.; Default; SURFACE FINISH; PART NUMBER; IN INCHES; CHECKED; DRAWN NLS; TOLERANCES ARE:; DESCRIPTION; MACHINED FILLETS 0.015 MAX; PLOT DATE; .XXX; DIMENSIONS ARE; DRAWING NUMBER; FRACTIONS; DATE; NO MODIFICATION OF SPECIFIED; SHEET; BREAK SHARP EDGES 0.005 MIN; DECIMALS; ANGLES; Notes: 1. MATERIAL: PVC PVC Type I Rod FINISH:; SCALE 1 : 1; SECTION D-D; MAX; R.13 MAX; REVISIONS; 2X R0.005 MAX; 2X R0.015 MAX; DETAIL E SCALE 1 : 1; 2X R0.005 MAX 32; DETAIL F SCALE 1 : 1

ZONE | REV. | DESCRIPTION | DATE | APPROVED
C6 | A | loosen dim tolerance frm 4.477-4.479 for ease of manufacture | 7/28/2020
B4, C1, C3, C4, C5, D5 | B | loosen dim tolerance frm 2.271-2.273 for ease of manufacture, add in concentricity tolerance, Add ID chamfer for ease of assembly, Decrease length by 0.07 for thicker case, Increase large piston seal dia. by 0.005. | 8/21/2020

to virtual sharp

NOAA-PMEL
Engineering Division
Low Cost Profiler Piston

UNLESS OTHERWISE SPECIFIED

THIRD ANGLE PROJECTION

7600 Sand Point Wy NE
Seattle, WA 98115

DIMENSIONS OR MATERIALS IS
ALLOWED UNLESS APPROVED
BY NOAA ENGINEERS.
DO NOT SCALE DRAWING

PRODUCT
Low Coast Profiler
CONFIGURATION

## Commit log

2025-10-01 Add Mechanicals and background
    [R_000450.SLDDRW, R_000450.sldprt, R_000521.SLDDRW, R_000521.sldprt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]
2025-10-24 Add in missing assembly drawing PDFs
